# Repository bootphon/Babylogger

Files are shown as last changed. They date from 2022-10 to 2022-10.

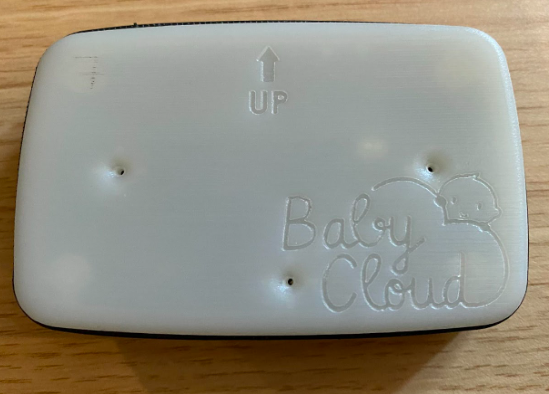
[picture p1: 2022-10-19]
pictures/babylogger.png

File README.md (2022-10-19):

# Babylogger

What is the BabyLogger?
=======================
The BabyLogger is a device used by researchers to record the child’s interactions in a secure way and to extract the audio and actimetric information.

Organization
============
All you need to fabricate a new device :
- [src](https://github.com/bootphon/Babylogger/tree/main/src) : babylogger software.
- [doc](https://github.com/bootphon/Babylogger/tree/main/doc) : the babyloger documentation with all the plans of the Babylogger box and the electronic card.

Reference
=========

- [Babylogger website](https://docs.babycloudlab.com/).

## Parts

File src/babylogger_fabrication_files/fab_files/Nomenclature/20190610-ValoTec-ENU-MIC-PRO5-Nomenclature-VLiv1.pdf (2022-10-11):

# 20190610-ValoTec-ENU-MIC-PRO5-Nomenclature-VLiv1.xlsx

Client | EHESS
Projet | ENU-MIC-PRO5
Phase | Prototype
Revision | VLiv1
Date | 10/06/2019
Designator | Description | Manufacturer | Reference Manufacturer | Supplier | Reference Supplier | Quantity | Implemented | Price | Sous total | Price /100 | Sous total | Price /1000 | Sous total | PackageRefere nce | #Column Name Error:Technology | Value | Voltage | Tolerance | #Column Name Error:Power | #Column Name Error:Resistan ce | #Column Name Error:Courant | RoHS
C1, C3 | Polarized Capacitor | AVX | TAJA106K010RNJ | Farnell | 197130 | | 2 Yes | 0,431 € | 0,86 € | 0,223 € | 0,45 € | 0,0853 € | 0,17 € | Tantal-A | | 10µF | 10V | ±10% | | | | Yes
C2, C4, C15, C18, C19, C21, C27, C28, C29, C31, C32, C35, C37, C39, C40, C41, C42, C43, C47, C49, C53, C66, C67 | Capacitor | AVX | 06035C104KAT2A | Farnell | 1301804 | 23 | Yes | 0,0284 € | 0,65 € | 0,0176 € | 0,40 € | 0,0095 € | 0,22 € | 0603 | | 100nF | 50V | ± 10% | | | | Yes
C5, C8 | Capacitor | MURATA | GRM188R61C475KAAJD | Farnell | 2611924 | | 2 No | 0,339 € | 0,00 € | 0,151 € | 0,00 € | 0,0918 € | 0,00 € | 0603 | | NC | 16V | ± 20% | | | | Yes
C6, C7, C17, C30 | Capacitor | MURATA | GRM188R61C475KAAJD | Farnell | 2611924 | | 4 Yes | 0,339 € | 1,36 € | 0,151 € | 0,60 € | 0,0918 € | 0,37 € | 0603 | | 4.7uF | 16V | ± 20% | | | | Yes
C9, C12 | Capacitor | YAGEO | CC0603KRX5R7BB225 | Farnell | 1458897 | | 2 No | 0,158 € | 0,00 € | 0,0897 € | 0,00 € | 0,0531 € | 0,00 € | 0603 | | NC | 16V | ± 10% | | | | Yes
C10, C11 | Capacitor | YAGEO | CC0603KRX5R7BB225 | Farnell | 1458897 | | 2 Yes | 0,158 € | 0,32 € | 0,0897 € | 0,18 € | 0,0531 € | 0,11 € | 0603 | | 2.2µF | 16V | ± 10% | | | | Yes
C13, C33, C34, C36, C55, C57 | Capacitor | TDK | CGA3E2X5R1A105K080AA | Farnell | 2768405 | | 6 Yes | 0,151 € | 0,91 € | 0,0731 € | 0,44 € | 0,0393 € | 0,24 € | 0603 | | 1µF | 10V | ± 10% | | | | Yes
C14 | Capacitor | TDK | CGA3E3X7R1H224K080AB | Farnell | 2210924 | | 1 Yes | 0,151 € | 0,15 € | 0,0924 € | 0,09 € | 0,0491 € | 0,05 € | 0603 | | 220nF | 50V | ± 10% | | | | Yes
C16 | Capacitor | KEMET | C1206C225K4RACTU | Farnell | 9227911 | | 1 Yes | 0,186 € | 0,19 € | 0,0848 € | 0,08 € | 0,0612 € | 0,06 € | 1206 | | 2.2µF | 16V | ± 10% | | | | Yes
C20 | Capacitor | AVX | 06035C100KAT2A | Farnell | 2332633 | | 1 Yes | 0,256 € | 0,26 € | 0,106 € | 0,11 € | 0,0408 € | 0,04 € | 0603 | | 10pF | 50V | ± 5% | | | | Yes
C22 | Capacitor | AVX | 06035C104KAT2A | Farnell | 1301804 | | 1 No | 0,0284 € | 0,00 € | 0,0176 € | 0,00 € | 0,0095 € | 0,00 € | 0603 | | 100nF | 50V | ± 10% | | | | Yes
C24, C46 | Capacitor | AVX | 06031A101JAT2A | Farnell | 1740605 | | 2 Yes | 0,0626 € | 0,13 € | 0,0273 € | 0,05 € | 0,0124 € | 0,02 € | 0603 | | 100pF | 100V | ± 5% | | | | Yes
C25, C26 | Capacitor | AVX | 04023J4R3BBSTR | Farnell | 1702754 | | 2 Yes | 0,569 € | 1,14 € | 0,306 € | 0,61 € | 0,208 € | 0,42 € | 0402 | | 4.3pF | 25V | ± 0.1pF | | | | Yes
C38 | Capacitor | AVX | 0805YD106KAT2A | Farnell | 1658880 | | 1 Yes | 0,175 € | 0,18 € | 0,10 € | 0,10 € | 0,0585 € | 0,06 € | 0805 | | 10µF | 16V | ± 10% | | | | Yes
C44 | Capacitor | AVX | 06033C103KAT2A | Farnell | 2280646 | | 1 Yes | 0,128 € | 0,13 € | 0,0427 € | 0,04 € | 0,0128 € | 0,01 € | 0603 | | 10nF | 25V | ±10% | | | | Yes
C45 | Capacitor | MURATA | GRT31CR71E106KE13L | Farnell | 2672218 | | 1 Yes | 0,527 € | 0,53 € | 0,264 € | 0,26 € | 0,109 € | 0,11 € | 1206 | | 10uF | 25V | 10% | | | | Yes
C48, C50, C54, C69 | Capacitor | KEMET | C0805C105K3RACTU | Farnell | 1637035 | | 4 Yes | 0,0976 € | 0,39 € | 0,0598 € | 0,24 € | 0,0299 € | 0,12 € | 0805 | | 1uF | 25V | ± 10% | | | | Yes
C56 | Capacitor | Murata | GRM21BR60J107ME15L | Farnell | 2494476 | | 1 Yes | 1,61 € | 1,61 € | 1,16 € | 1,16 € | 0,81 € | 0,81 € | 0805 | | 100uF | 6.3V | ± 20% | | | | Yes
C59, C60 | Capacitor | MURATA | GRM21BR61E106KA73L | Farnell | 1735530 | | 2 Yes | 0,395 € | 0,79 € | 0,233 € | 0,47 € | 0,124 € | 0,25 € | 0805 | | 10uF | 25V | ± 10% | | | | Yes
C61, C62 | Capacitor | MURATA | ZRB18AR61E106ME01L | Farnell | 2469398 | | 2 Yes | 0,448 € | 0,90 € | 0,263 € | 0,53 € | 0,14 € | 0,28 € | 0603 | | 10uF | 25V | ± 20% | | | | Yes
C63, C64, C65 | Capacitor | TDK | C2012X5R1C226M125AC | Farnell | 2525135 | | 3 Yes | 0,658 € | 1,97 € | 0,316 € | 0,95 € | 0,188 € | 0,56 € | 0805 | | 22uF | 16V | ± 10% | | | | Yes
C68 | Capacitor | JOHANSON DIELECTRICS | 202S41W222KV4E | Farnell | 1886057 | | 1 Yes | 0,342€ | 0,34 € | 0,202 € | 0,20 € | 0,0988 € | 0,10 € | 1210 | | 2.2nF | 2kV | ± 10% | | | | Yes
D1 | LED | Wurth Elektronik | 150080RS75000 | DigiKey | 732-4984-1-ND | | 1 Yes | 0,16€ | 0,16 € | 0,12820 € | 0,13 € | 0,11044 € | 0,11 € | 0805 | | | | | | | | Yes
D2 | LED | Wurth Elektronik | 150080GS75000 | Farnell | 2322076 | | 1 Yes | 0,242 € | 0,24 € | 0,168 € | 0,17 € | 0,152 € | 0,15 € | 0805 | | | | | | | | Yes
EXT1 | Batterie | Jauch | LP543450JE | Jauch | LP543450JE | | 1 No | 15 € | 0,00 € | 15 € | 0,00 € | 15 € | 0,00 €
FD1, FD2, FD3, FD4, FD6, FD7, FD8 | Fiducial Hole | | | | | | 7 Yes | 0 | 0,00 € | 0 | 0,00 € | 0 | 0,00 € | | | | | | | | | Yes
J1 | WR-COM Micro USB 2.0 Type AB Horizontal | Wurth Elektronik | 629105150921 | Farnell | 2470823 | | 1 Yes | 1,62 € | 1,62 € | 1,38 € | 1,38 € | 1,18 € | 1,18 € | | | | | | | | | Yes
J2 | WR-CRD Micro SD Card Connector Push & Push - 8 pins | Wurth Elektronik | 693071010811 | Farnell | 2081363 | | 1 Yes | 2,23 € | 2,23 € | 1,89 € | 1,89 € | 1,68 € | 1,68 € | | | | | | | | | Yes
L1 | Shielded Power Inductor | TDK | MPZ1608S300A | Farnell | 1669744 | | 1 Yes | 0,0771 € | 0,08 € | 0,0399 € | 0,04 € | 0,0232 € | 0,02 € | 0603 | | 30R/100Mhz | | ± 10ohm | | | | Yes
L2 | Inductor | Coilcraft | XFL4020-152MEB | Farnell | 994-XFL4020-152MEB | | 1 Yes | 1,93 € | 1,93 € | 1,54 € | 1,54 € | 0,858 € | 0,86 € | 4mm x 4mm x 2.1mm | | 1.5µH | | | | | | Yes
M1 | Microphone | PUI Audio. Inc | POM-2244P-C33-R | DigiKey | 668-1400-ND | | 1 Yes | 1,86 € | 1,86 € | 1,17 € | 1,17 € | 0,95590 € | 0,96 € | POM-2244P-C33-R | | | | | | | | Yes
P1 | Header, 2-Pin | MOLEX | 53261-0271 | Farnell | 2118430 | | 1 Yes | 0,686 € | 0,69 € | 0,541 € | 0,54 € | 0,488 € | 0,49 € | | | | | | | | | Yes
P2 | Header, 6-Pin | MOLEX | 78171-5006 | Mouser | 538-78171-5006 | | 1 Yes | 0,672 € | 0,67 € | 0,507 € | 0,51 € | 0,369 € | 0,37 € | | | | | | | | | Yes
P4 | Header, 4-Pin | Molex | 0524180410 | DigiKey | WM9200-ND | | 1 Yes | 0,52 € | 0,52 € | 0,37 € | 0,37 € | 0,26 € | 0,26 € | | | | | | | | | Yes
P5 | Header, 4-Pin | Molex | 0532900480 | DigiKey | WM9208-ND | | 1 Yes | 0,38 € | 0,38 € | 0,27 € | 0,27 € | 0,24 € | 0,24 € | | | | | | | | | Yes
P7 | Header, 7-Pin | Molex | 78171-5007 | Mouser | 538-78171-5007 | | 1 Yes | 0,803 € | 0,80 € | 0,606 € | 0,61 € | 0,441 € | 0,44 €
P8 | | | | | | | 1 | | 0,00 € | | 0,00 € | | 0,00 €
Q1 | MOSFET-P | VISHAY | SI2307CDS-T1-GE3 | Farnell | 1779262 | | 1 No | 0,40 € | 0,00 € | 0,261 € | 0,00 € | 0,187 € | 0,00 € | SOT23-3 | | | Vgs(th) = -1V | | | | | Yes
Q2, Q3 | MOSFET-N | FAIRCHILD SEMICONDUCTOR | 2N7002 | Farnell | 9845313 | | 2 Yes | 0,186 € | 0,37 € | 0,078 € | 0,16 € | 0,0475 € | 0,10 € | SOT23-3 | | | Vgs(th) = 2.1V | | | | | Yes
Q4 | MOSFET-P | NEXPERIA | PMV65XP,215 | Farnell | 1758119 | | 1 Yes | 0,335 € | 0,34 € | 0,163 € | 0,16 € | 0,12 € | 0,12 € | SOT23-3 | | | Vgs(th) = -750mV | | | | | Yes
R1, R28, R47, R75, R81, R92, R93, R94, R95, R96, R97 | Resistance | MULTICOMP | MC0603SAF0000T5E | Farnell | 2309111 | 11 | No | 0,0089 € | 0,00 € | 0,0072 € | 0,00 € | 0,0043 € | 0,00 € | 0603 | | 0R, NC, 0R, NC, NC, NC, NC, NC, NC, NC, NC | 50V | 1% | | | | Yes
R2, R9, R29, R30, R33, R38, R39, R40, R48, R50, R55, R60, R61, R77, R78, R79, R80, R82, R83, R86, R91 | Resistance | MULTICOMP | MC0603SAF0000T5E | Farnell | 2309111 | 21 | Yes | 0,0089 € | 0,19 € | 0,0072 € | 0,15 € | 0,0043 € | 0,09 € | 0603 | | 0R | 50V | 1% | | | | Yes
R3, R4, R5, R18, R24, R26, R34, R54, R68, R73, R74, R84, R87 | Resistance | Vishay | CRCW060310K0FKEA | Farnell | 1469748 | 13 | Yes | 0,0219 € | 0,28 € | 0,0122 € | 0,16 € | 0,0068 € | 0,09 € | 0603 | | 10k | 75V | ± 1% | | | | Yes
R6 | Resistance | Vishay | ERA3AEB1541V | Farnell | 1809752 | | 1 Yes | 0,242 € | 0,24 € | 0,114 € | 0,11 € | 0,0619 € | 0,06 € | 0603 | | 1k54 | 75V | ± 1% | | | | Yes
R7 | Resistance | Vishay | CRCW060369K8FKEA | Farnell | 2138483 | | 1 Yes | 0,0245 € | 0,02 € | 0,0166 € | 0,02 € | 0,0104 € | 0,01 € | 0603 | | 69k8 | 75V | ± 1% | | | | Yes
R8 | Resistance | VISHAY | CRCW06032K00FKEA | Farnell | 1469764 | | 1 Yes | 0,0181 € | 0,02 € | 0,0139 € | 0,01 € | 0,0088 € | 0,01 € | 0603 | | 2k | 75V | ± 1% | | | | Yes
R10, R71 | Resistance | Vishay | CRCW0603100KFKEA | Farnell | 1469649 | | 2 No | 0,0542 € | 0,00 € | 0,0217 € | 0,00 € | 0,0084 € | 0,00 € | 0603 | | 100k, NC | 75V | ± 1% | | | | Yes
R11, R12 | Resistance | MULTICOMP | MCWR06X4701FTL | Farnell | 2447385 | | 2 Yes | 0,0054 € | 0,01 € | 0,0032 € | 0,01 € | 0,0018 € | 0,00 € | 0603 | | 4.7k | 50V | 1% | | | | Yes
R13, R15, R16, R20, R21, R23, R49, R51, R57 | Resistance | VISHAY | CRCW06031K00FKEA | Farnell | 1469740 | | 9 Yes | 0,0419 € | 0,38 € | 0,0172 € | 0,15 € | 0,0073 € | 0,07 € | 0603 | | 1k | 75V | ±1%, ±1%, ±1%, ± 1%, ± 1%, ± 1%, ±1%, ±1%, ±1% | | | | Yes
R14, R90 | Resistance | WELWYN | HVC2010-1M0FT3 | Farnell | 2340627 | | 2 Yes | 1,34 € | 2,68 € | 0,921 € | 1,84 € | 0,716 € | 1,43 € | 2010 | | 1M | 2kV | ± 1% | | | | Yes
R17 | Resistance | VISHAY | WSL0603R0100FEA | Farnell | 2112794 | | 1 Yes | 0,961 € | 0,96 € | 0,40 € | 0,40 € | 0,332 € | 0,33 € | 0603 | | 10mR | 75V | ±1% | | | | Yes
R22, R35, R36, R37 | Resistance | | | | | | 4 No | 0 | 0,00 € | 0 | 0,00 € | 0 | 0,00 € | 0603 | | NC | | | | | | Yes
R31, R32 | Resistance | YAGEO | RC0603FR-072K2L | Farnell | 9238522 | | 2 Yes | 0,0239 € | 0,05 € | 0,0183 € | 0,04 € | 0,0107 € | 0,02 € | 0603 | | 2.2k | 75V | 1% | | | | Yes
R41, R70, R72, R76, R85, R98, R99 | Resistance | Vishay | CRCW0603100KFKEA | Farnell | 1469649 | | 7 Yes | 0,0542 € | 0,38 € | 0,0217 € | 0,15 € | 0,0084 € | 0,06 € | 0603 | | 100k | 75V | ± 1% | | | | Yes
R42, R43, R44, R45, R46 | Resistance | Vishay | CRCW060347K0FKEA | Farnell | 1469811 | | 5 Yes | 0,0202 € | 0,10 € | 0,0202 | 0,10 € | 0,0084 € | 0,04 € | 0603 | | 47k | 75V | ± 1% | | | | Yes
R52 | Resistance | MULTICOMP | MCWR06X4700FTL | Farnell | 2447374 | | 1 Yes | 0,0034 € | 0,00 € | 0,002 € | 0,00 € | 0,0011 € | 0,00 € | 0603 | | 470R | 50V | 1% | | | | Yes
R53, R56 | Resistance | VISHAY | CRCW06031M00FKEA | Farnell | 1469746 | | 2 Yes | 0,0419 € | 0,08 € | 0,0172 € | 0,03 € | 0,0073 € | 0,01 € | 0603 | | 1M | 75V | 1% | | | | Yes
R58, R59 | Resistance | VISHAY | CRCW060322K0FKEA | Farnell | 1469779 | | 2 Yes | 0,0542 € | 0,11 € | 0,0217 € | 0,04 € | 0,0084 € | 0,02 € | 0603 | | 22k, ? | 75V | ± 1% | | | | Yes
R88 | Resistance | PANASONIC ELECTRONIC COMPONENTS | ERJ3EKF4703V | Farnell | 2303289 | | 1 Yes | 0,0333 € | 0,03 € | 0,0243 € | 0,02 € | 0,01 € | 0,01 € | 0603 | | 470k | 75V | ± 1% | | | | Yes
R89 | Resistance | Vishay | CRCW0603150KFKEA | Farnell | 1469759 | | 1 Yes | 0,0227 € | 0,02 € | 0,0175 € | 0,02 € | 0,0095 € | 0,01 € | 0603 | | 150k | 75V | ± 1% | | | | Yes
RT1 | Thermistor | LITTELFUSE | MM103J1F | Farnell | 2888868 | | 1 Yes | 1,27 € | 1,27 € | 0,723 € | 0,72 € | 0,617 € | 0,62 €
S1 | Switch | Panasonic | EVP-AKB11A | DigiKey | P17065CT-ND | | 1 Yes | 0,54 € | 0,54 € | 0,4256 € | 0,43 € | 0,4256 € | 0,43 € | EVP-AKB11A | | | | | | | | Yes
S3 | Switch | OMRON | B3U-1000P | Farnell | 1333652 | | 1 Yes | 0,68 € | 0,68 € | 0,618 € | 0,62 € | 0,448 € | 0,45 € | B3U-1000P | | | | | | | | Yes
T1, T2, T3, T5, T11 | Test point | VERO Technologies | 20-2137 | Farnell | 8731128 | | 5 No | 0,23€ | 0,00 € | 0,23€ | 0,00 € | 0,23€ | 0,00 € | | | | | | | | | Yes
U1 | Stand-Alone System Load Sharing and Li-Ion/Li-PolymerChargeur de batterie, Batterie 1 cellule Li-Pol, Entrée 6V, Charge 4,2V / 1,1A, DFN-10 | Microchip | MCP73833-AMI/MF | Farnell | 2709765 | | 1 Yes | 0,748 € | 0,75 € | 0,565 € | 0,57 € | 0,565 € | 0,57 € | DFN-10 | | | | | | | | Yes
U2 | Linear Voltage Regulator IC Positive Fixed 1 Output 3.3V 1A 6-DFN (3x3) | STMicroelectronics | LD39100PU33RY | Digikey | 497-16700-1-ND | | 1 Yes | 1,55 € | 1,55 € | 1,08 € | 1,08 € | 0,7 € | 0,70 € | 6-DFN | | | | | | | | Yes
U3 | Jauge de batterie, Li-Ion, Li-Pol, Alimentation 2,7V à 4,35V, Interface I2C, DFN-10 | STMICROELECTRONICS | STC3115AIQT | Farnell | 2770310 | | 1 Yes | 2,73 € | 2,73 € | 1,75 € | 1,75 € | 1,19 € | 1,19 € | DFN-10 | | | | | | | | Yes
U4 | Capacitive digital sensor for relative humidity and temperature | STMicroelectronics | HTS221 | Farnell | 2433085 | | 1 Yes | 1,44 € | 1,44 € | 1,36 € | 1,36 € | 1,30 € | 1,30 € | HLGA-6L | | | | | | | | Yes
U5 | Module MEMS, iNEMO, Gyroscope 3 axes, Accéléromètre 3 axes, 1.71 V, 3.6 V, LGA, 14 Broche(s) | STMICROELECTRONICS | LSM6DSLTR | Farnell | 2761748 | | 1 Yes | 3,29 € | 3,29 € | 2,59 € | 2,59 € | 1,80 € | 1,80 € | LGA-14L | | | | | | | | Yes
U6 | MCU ARM, STM32 Family STM32L4 Series Microcontrollers, ARM Cortex-M4, 32 bits, 80 MHz, 1 MB, 320 KB | STMICROELECTRONICS | STM32L4A6RGT7 | Farnell | 2758831 | | 1 Yes | 10,95 € | 10,95 € | 8,03 € | 8,03 € | 6,54 € | 6,54 € | LQFP64 | | | | | | | | Yes
U7 | EEPROM Memory IC 2Kb (256 x 8) I²C 400kHz 900ns 8-TSSOP | STMicroelectronics | M24C02-WDW6TP | Digikey | 497-4926-1-ND | | 1 Yes | 0,12 € | 0,12 € | 0,099 € | 0,10 € | 0,093 € | 0,09 € | 8-TSSOP | | | | | | | | Yes
U8 | 1.8V, Nanopower, PUSH-PULL OUTPUT COMPARATOR | Texas Instruments | TLV3491AIDBVTG4 | Farnell | 1207299 | | 1 Yes | 1,19 € | 1,19 € | 0,646 € | 0,65 € | 0,646 € | 0,65 € | SOT23-5 | | | | | | | | Yes
U9 | Préamplificateur Microphone | MAXIM INTEGRATED PRODUCTS | MAX4466EXK+T | Farnell | 2514501 | | 1 Yes | 0,393 € | 0,39 € | 0,317 € | 0,32 € | 0,297 € | 0,30 € | | | | | | | | | Yes
U10, U11, U12, U17 | MEMS audio sensor omnidirectional digital microphone | STMicroelectronics | MP34DT06JTR | Farnell | 2980885 | | 4 Yes | 1,56 € | 6,24 € | 1,09 € | 4,36 € | 0,864 € | 3,46 € | HCLGA | | | | | | | | Yes
U14 | Very low power module for Bluetooth Smart v4.1 | STMicroelectronics | SPBTLE-RF | Mouser | 511-SPBTLE-R | | 1 Yes | 9,59 € | 9,59 € | 7,17 € | 7,17 € | 5,44 € | 5,44 € | | | | | | | | | Yes
U15 | SMD MODULE, ESP32-D0WDQ6, 32MBIT | Espressif Systems | ESP32-WROOM-32 | Digikey | 1904-1010-1-ND | | 1 Yes | 5,910 € | 5,91 € | 4,434 € | 4,43 € | 4,064 € | 4,06 € | ESP32-WROOM-32 | | | | | | | | Yes
U16 | 2-V to 16-V Buck-Boost Converter | Texas Instruments | TPS63070RNMR | Farnell | 2817379 | | 1 Yes | 2,12 € | 2,12 € | 1,50 € | 1,50 € | 1,09 € | 1,09 € | VQFN-15 | | | | | | | | Yes
Y1 | Crystal 32.768kHz | Epson Timing | NX3215SA | Digikey | 644-1156-1-ND | | 1 Yes | 0,57€ | 0,57 € | 0,4163€ | 0,42 € | 0,32865€ | 0,33 € | 3.2mmx1.5mm | | | | | | | | Yes

## TOTAL PRICE

## 79,56 € TOTAL PRICE

## 55,25 € TOTAL PRICE

42,23 €

# NOMENCLATURE ELECTRONIQUE

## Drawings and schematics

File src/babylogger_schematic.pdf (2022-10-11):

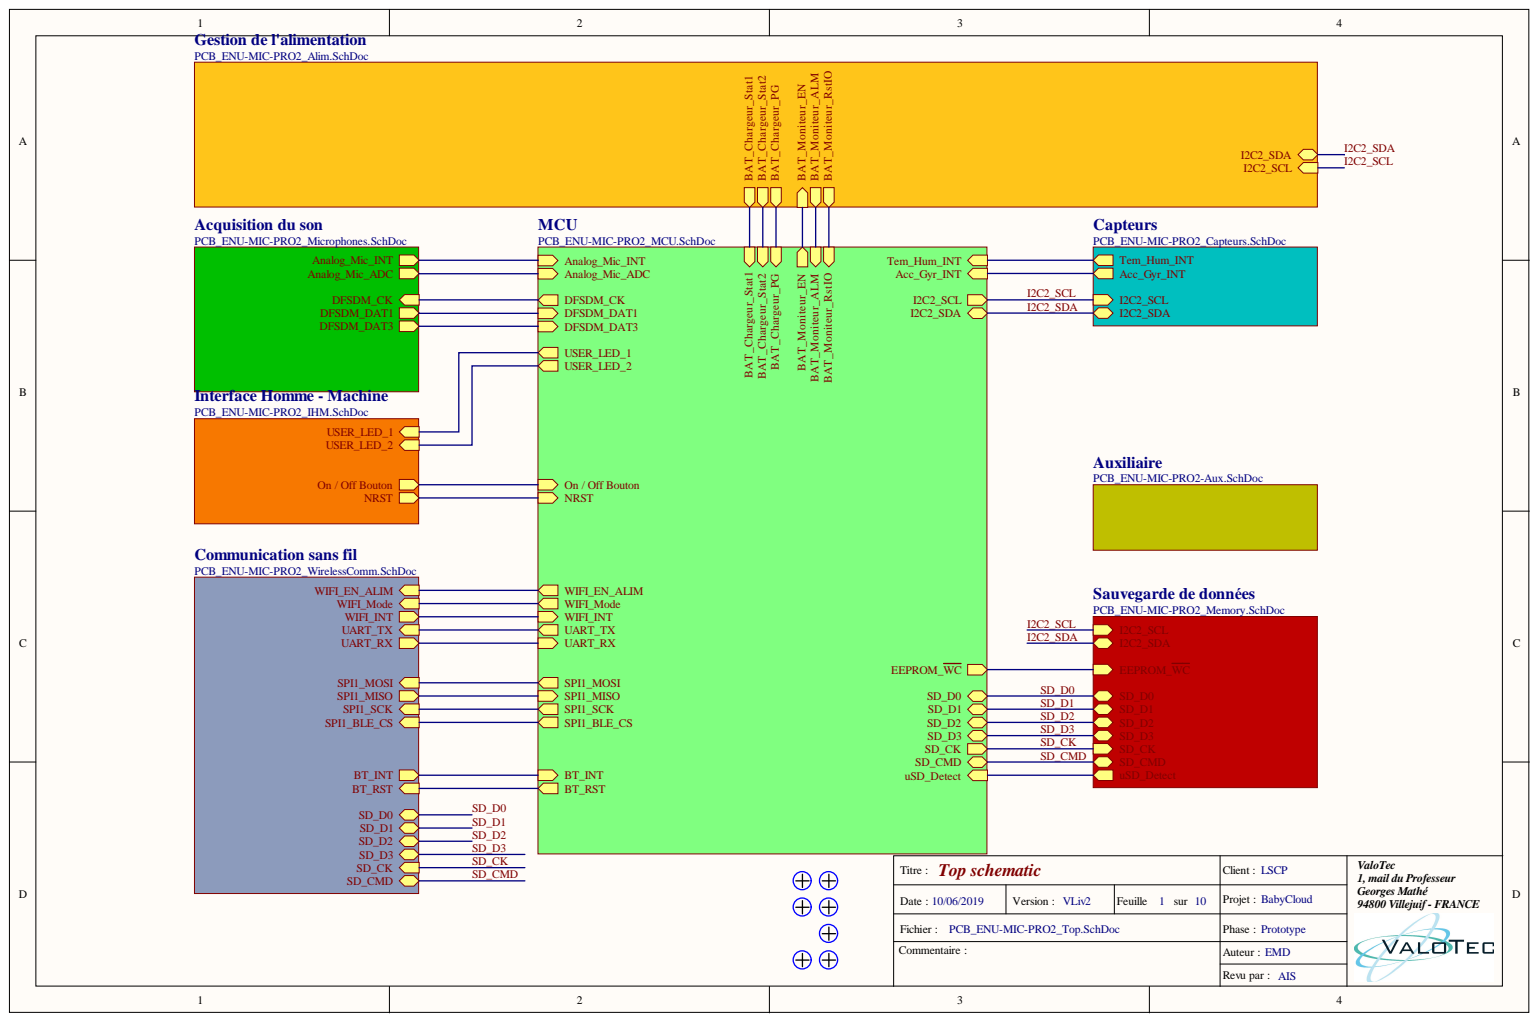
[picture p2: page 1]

Gestion de l'alimentation PCB_ENU-MIC-PRO2_Alim.SchDoc

Acquisition du son PCB_ENU-MIC-PRO2_Microphones.SchDoc

Interface Homme - Machine PCB_ENU-MIC-PRO2_IHM.SchDoc

Auxiliaire PCB_ENU-MIC-PRO2-Aux.SchDoc

Communication sans fil PCB_ENU-MIC-PRO2_WirelessComm.SchDoc

Sauvegarde de données PCB_ENU-MIC-PRO2_Memory.SchDoc

Top schematic Titre : | Client : LSCP | ValoTec 1, mail du Professeur Georges Mathé 94800 Villejuif - FRANCE

Date : 10/06/2019 | Version : VLiv2 | Feuille 1 sur 10 | Projet : BabyCloud

Fichier : PCB_ENU-MIC-PRO2_Top.SchDoc | | | Phase : Prototype

Commentaire : | | | Auteur : EMD

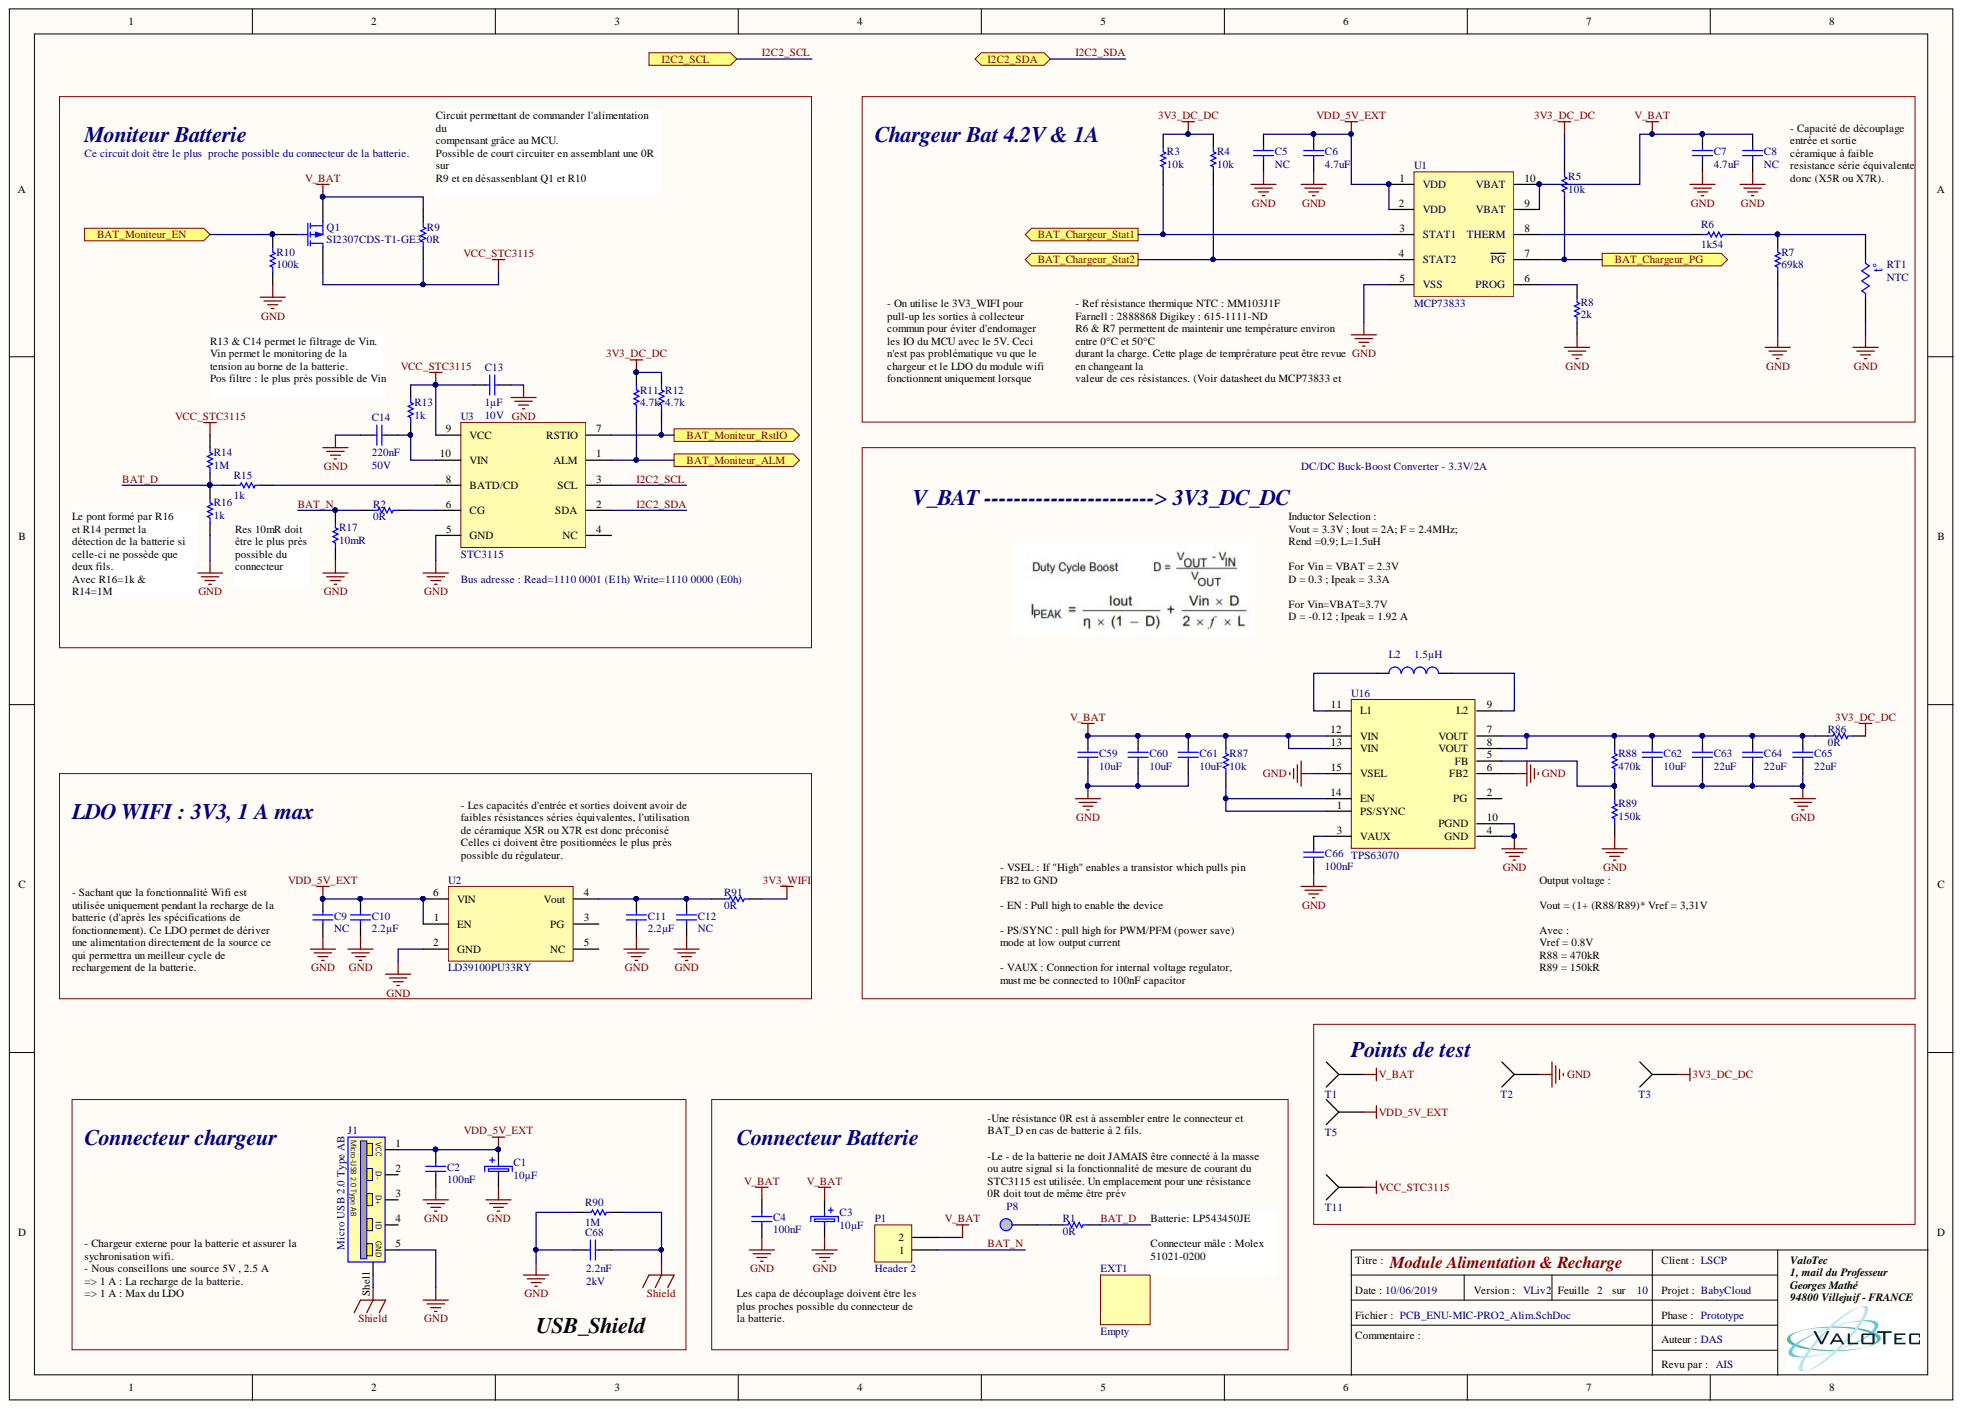
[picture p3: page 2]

Circuit permettant de commander l'alimentation
compensant grâce au MCU.
Possible de court circuiter en assemblant une 0R
sur
R9 et en désassenblant Q1 et R10

Ce circuit doit être le plus proche possible du connecteur de la batterie.

- On utilise le 3V3_WIFI pour
pull-up les sorties à collecteur
commun pour éviter d'endomager
les IO du MCU avec le 5V. Ceci
n'est pas problématique vu que le
chargeur et le LDO du module wifi
fonctionnent uniquement lorsque

- Ref résistance thermique NTC : MM103J1F
Farnell : 2888868 Digikey : 615-1111-ND
R6 & R7 permettent de maintenir une température environ
entre 0°C et 50°C
durant la charge. Cette plage de temprérature peut être revue
en changeant la
valeur de ces résistances. (Voir datasheet du MCP73833 et

R13 & C14 permet le filtrage de Vin.
Vin permet le monitoring de la
tension au borne de la batterie.
Pos filtre : le plus près possible de Vin

DC/DC Buck-Boost Converter - 3.3V/2A

Le pont formé par R16
et R14 permet la
détection de la batterie si
celle-ci ne possède que
deux fils.
Avec R16=1k &

Bus adresse : Read=1110 0001 (E1h) Write=1110 0000 (E0h)

- Les capacités d'entrée et sorties doivent avoir de
faibles résistances séries équivalentes, l'utilisation
de céramique X5R ou X7R est donc préconisé
Celles ci doivent être positionnées le plus près
possible du régulateur.

- VSEL : If "High" enables a transistor which pulls pin
FB2 to GND

- Sachant que la fonctionnalité Wifi est
utilisée uniquement pendant la recharge de la
batterie (d'après les spécifications de
fonctionnement). Ce LDO permet de dériver
une alimentation directement de la source ce
qui permettra un meilleur cycle de
rechargement de la batterie.

- EN : Pull high to enable the device

- PS/SYNC : pull high for PWM/PFM (power save)
mode at low output current

- VAUX : Connection for internal voltage regulator,
must me be connected to 100nF capacitor

-Une résistance 0R est à assembler entre le connecteur et
BAT_D en cas de batterie à 2 fils.

Micro USB 2.0 Type AB

Micro-USB 2.0 Type AB

-Le - de la batterie ne doit JAMAIS être connecté à la masse
ou autre signal si la fonctionnalité de mesure de courant du
STC3115 est utilisée. Un emplacement pour une résistance
0R doit tout de même être prév

- Chargeur externe pour la batterie et assurer la
sychronisation wifi.
- Nous conseillons une source 5V , 2.5 A
=> 1 A : La recharge de la batterie.
=> 1 A : Max du LDO

Titre : Module Alimentation & Recharge | Client : LSCP | ValoTec 1, mail du Professeur Georges Mathé 94800 Villejuif - FRANCE

Les capa de découplage doivent être les
plus proches possible du connecteur de
la batterie.

Date : 10/06/2019 | Version : VLiv2 | Feuille 2 sur 10 | Projet : BabyCloud

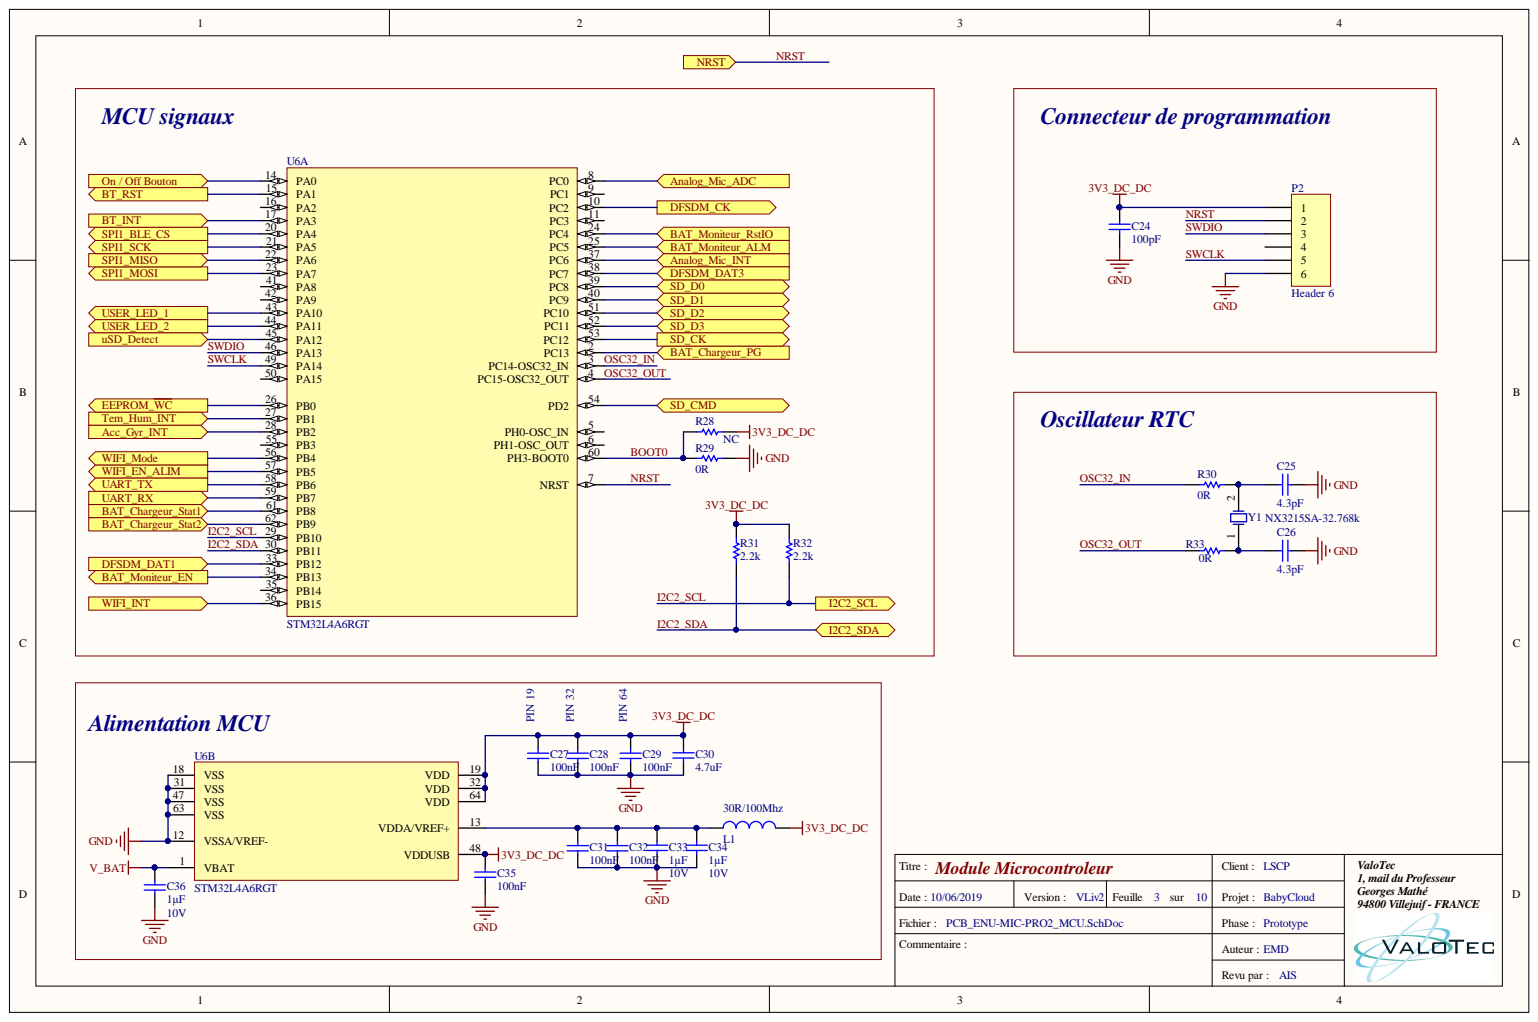
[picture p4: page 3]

Date : 10/06/2019 | Version : VLiv2 | Feuille 3 sur 10 | Projet : BabyCloud

Fichier : PCB_ENU-MIC-PRO2_MCU.SchDoc | | | Phase : Prototype
Commentaire : | | | Auteur : EMD

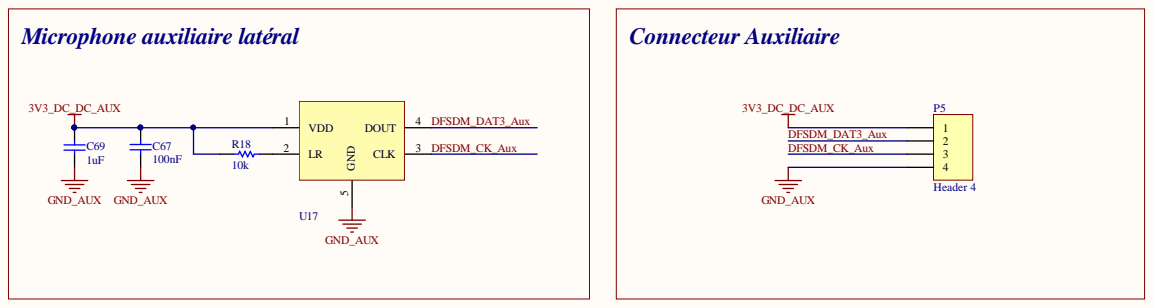
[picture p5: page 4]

Titre : P CB A uxiliaire | C lient : L S C P | Valo Te c 1 , m a il du Professe u r Ge o rg es Math é 948 0 0 Villeju if -FRA NCE

Da t e : 10/ 0 6/2 0 1 9 | Vers ion : VL iv2 | F e u ille 4 sur 1 0 | Proj e t : B a b y C lo u d

F ichi er : P C B _ENU-M I C-P RO2-A u x . S chDo c | | | P h a s e : Pro tot ype
C o mm e n t a ire : | | | Au t eur : DA SAI

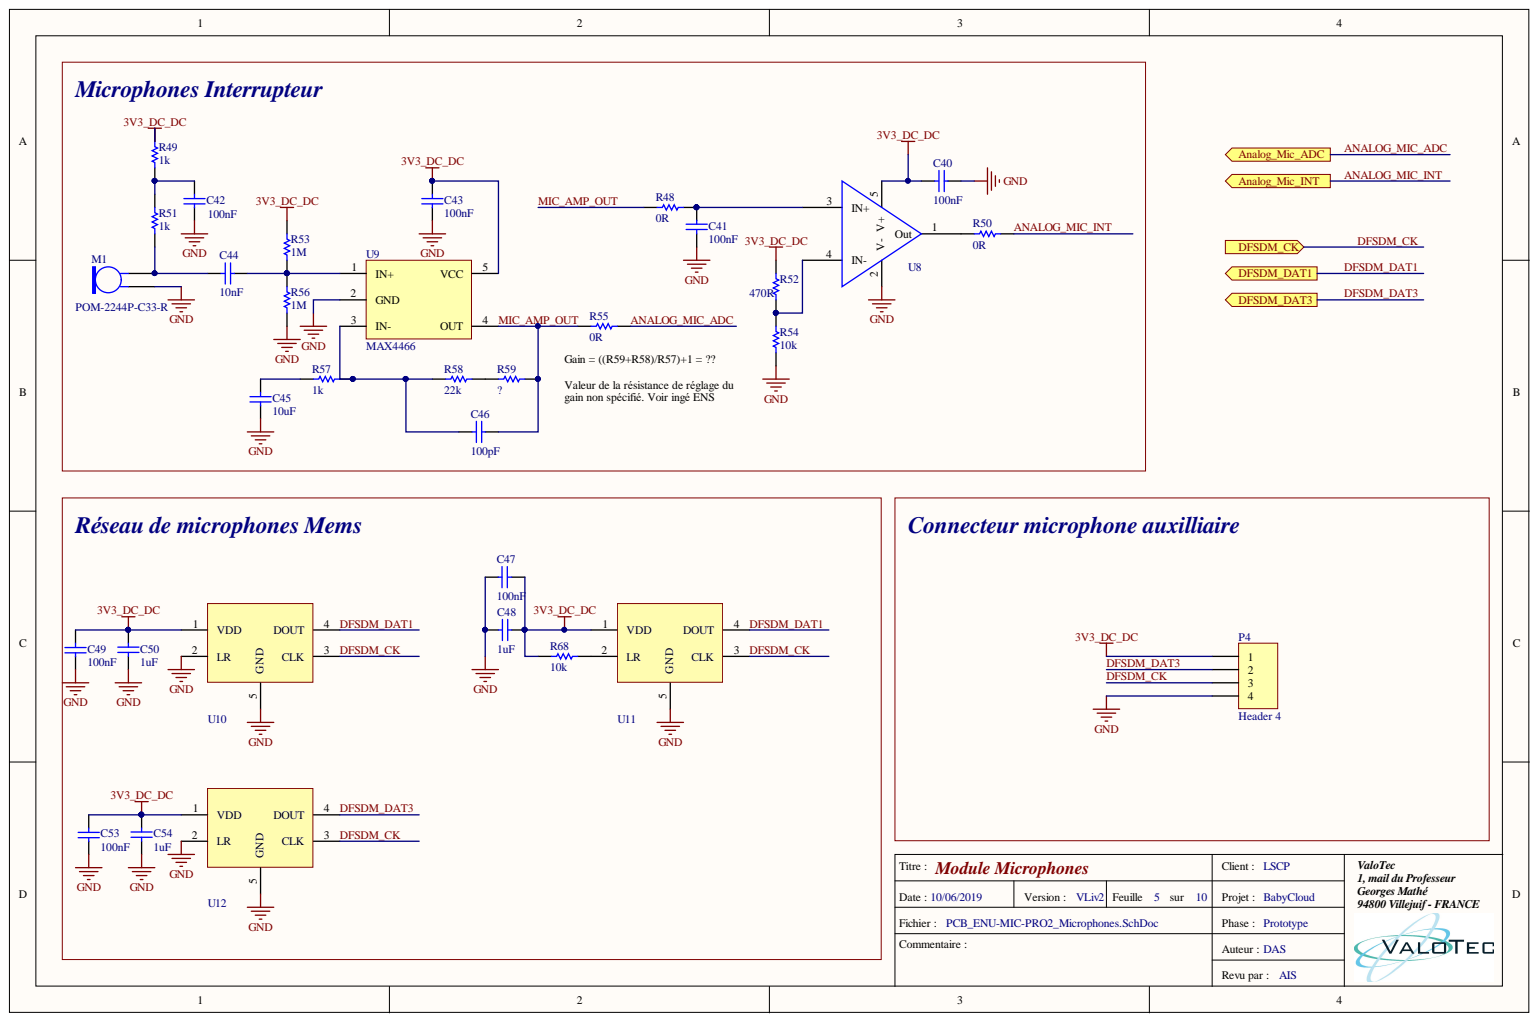
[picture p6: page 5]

Valeur de la résistance de réglage du
gain non spécifié. Voir ingé ENS

Réseau de microphones Mems

Titre : Module Microphones | Client : LSCP | ValoTec 1, mail du Professeur Georges Mathé 94800 Villejuif - FRANCE

Date : 10/06/2019 | Version : VLiv2 | Feuille 5 sur 10 | Projet : BabyCloud

Fichier : PCB_ENU-MIC-PRO2_Microphones.SchDoc | | | Phase : Prototype
Commentaire : | | | Auteur : DAS

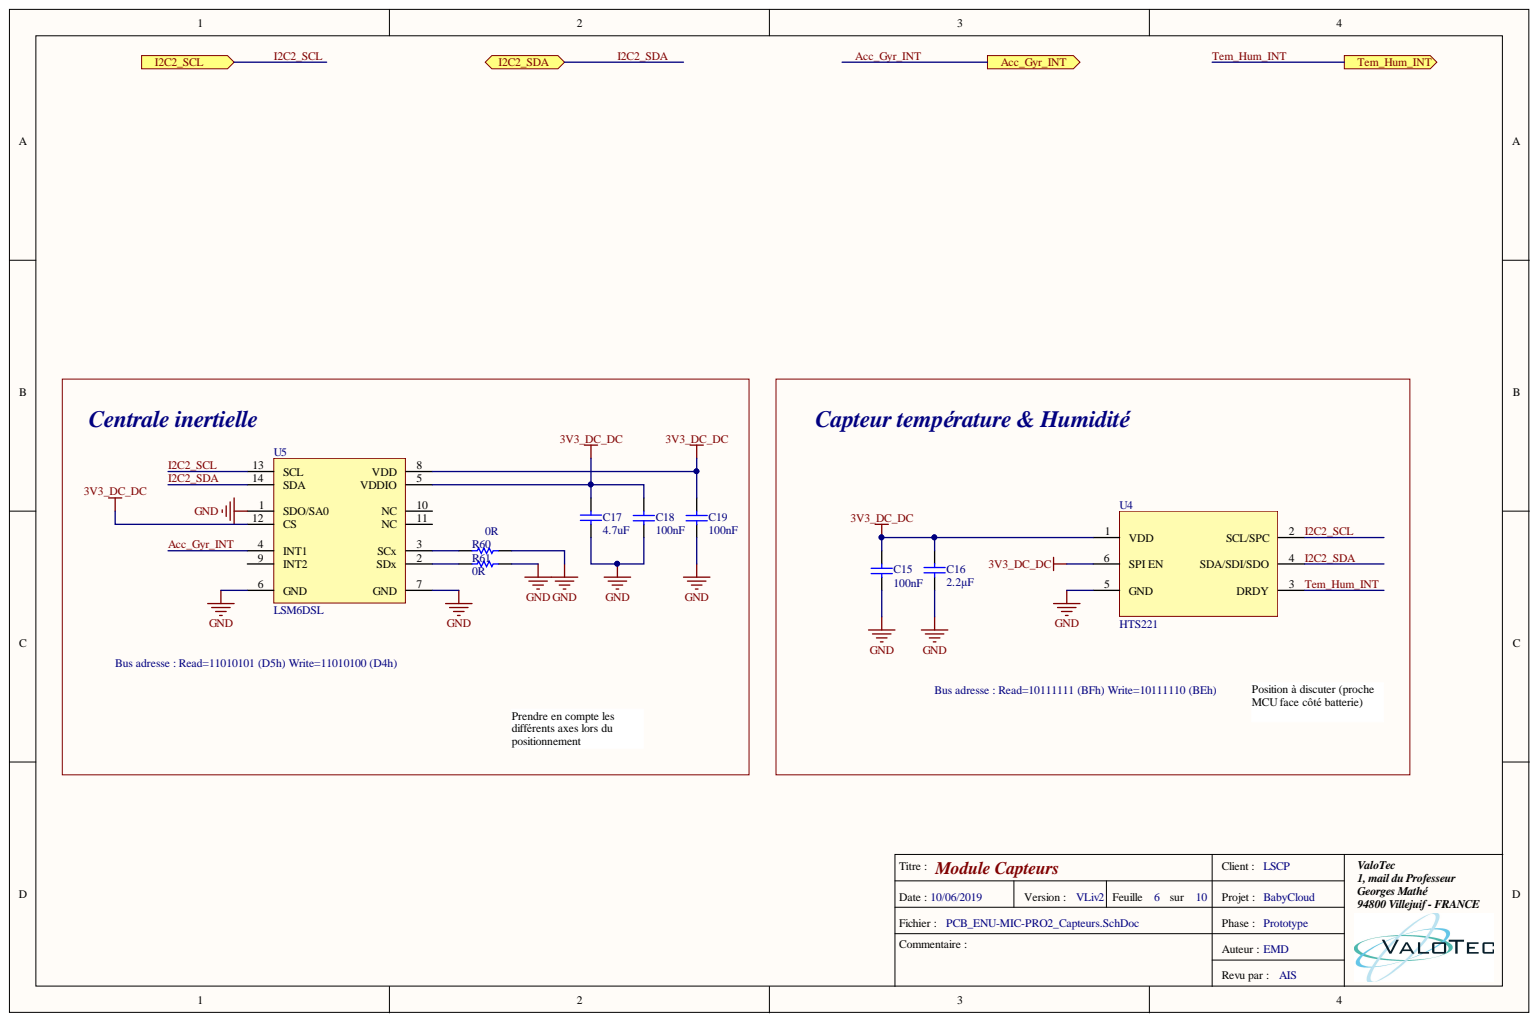
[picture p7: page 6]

Bus adresse : Read=11010101 (D5h) Write=11010100 (D4h)

MCU face côté batterie)
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

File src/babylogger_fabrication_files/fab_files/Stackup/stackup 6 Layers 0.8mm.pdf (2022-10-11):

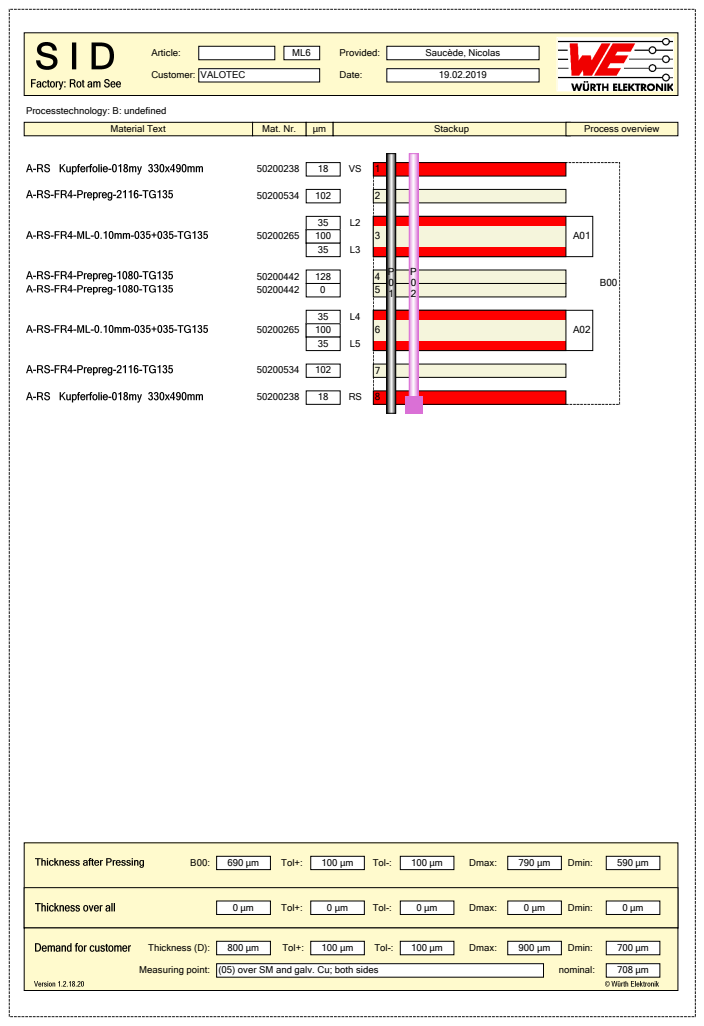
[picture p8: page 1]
Article:; Customer:; VALOTEC; Provided:; Saucède, Nicolas; Date:; Processtechnology: B: undefined; Material Text; Mat. Nr.; Stackup; Process overview; Tol+:; Tol-:; Dmax:; Dmin:; Thickness (D):; Measuring point:; (05) over SM and galv. Cu; both sides; nominal:

35 | L2 | 3 | | A01
50200265 | 100

35 | L4 | 6 | | A02

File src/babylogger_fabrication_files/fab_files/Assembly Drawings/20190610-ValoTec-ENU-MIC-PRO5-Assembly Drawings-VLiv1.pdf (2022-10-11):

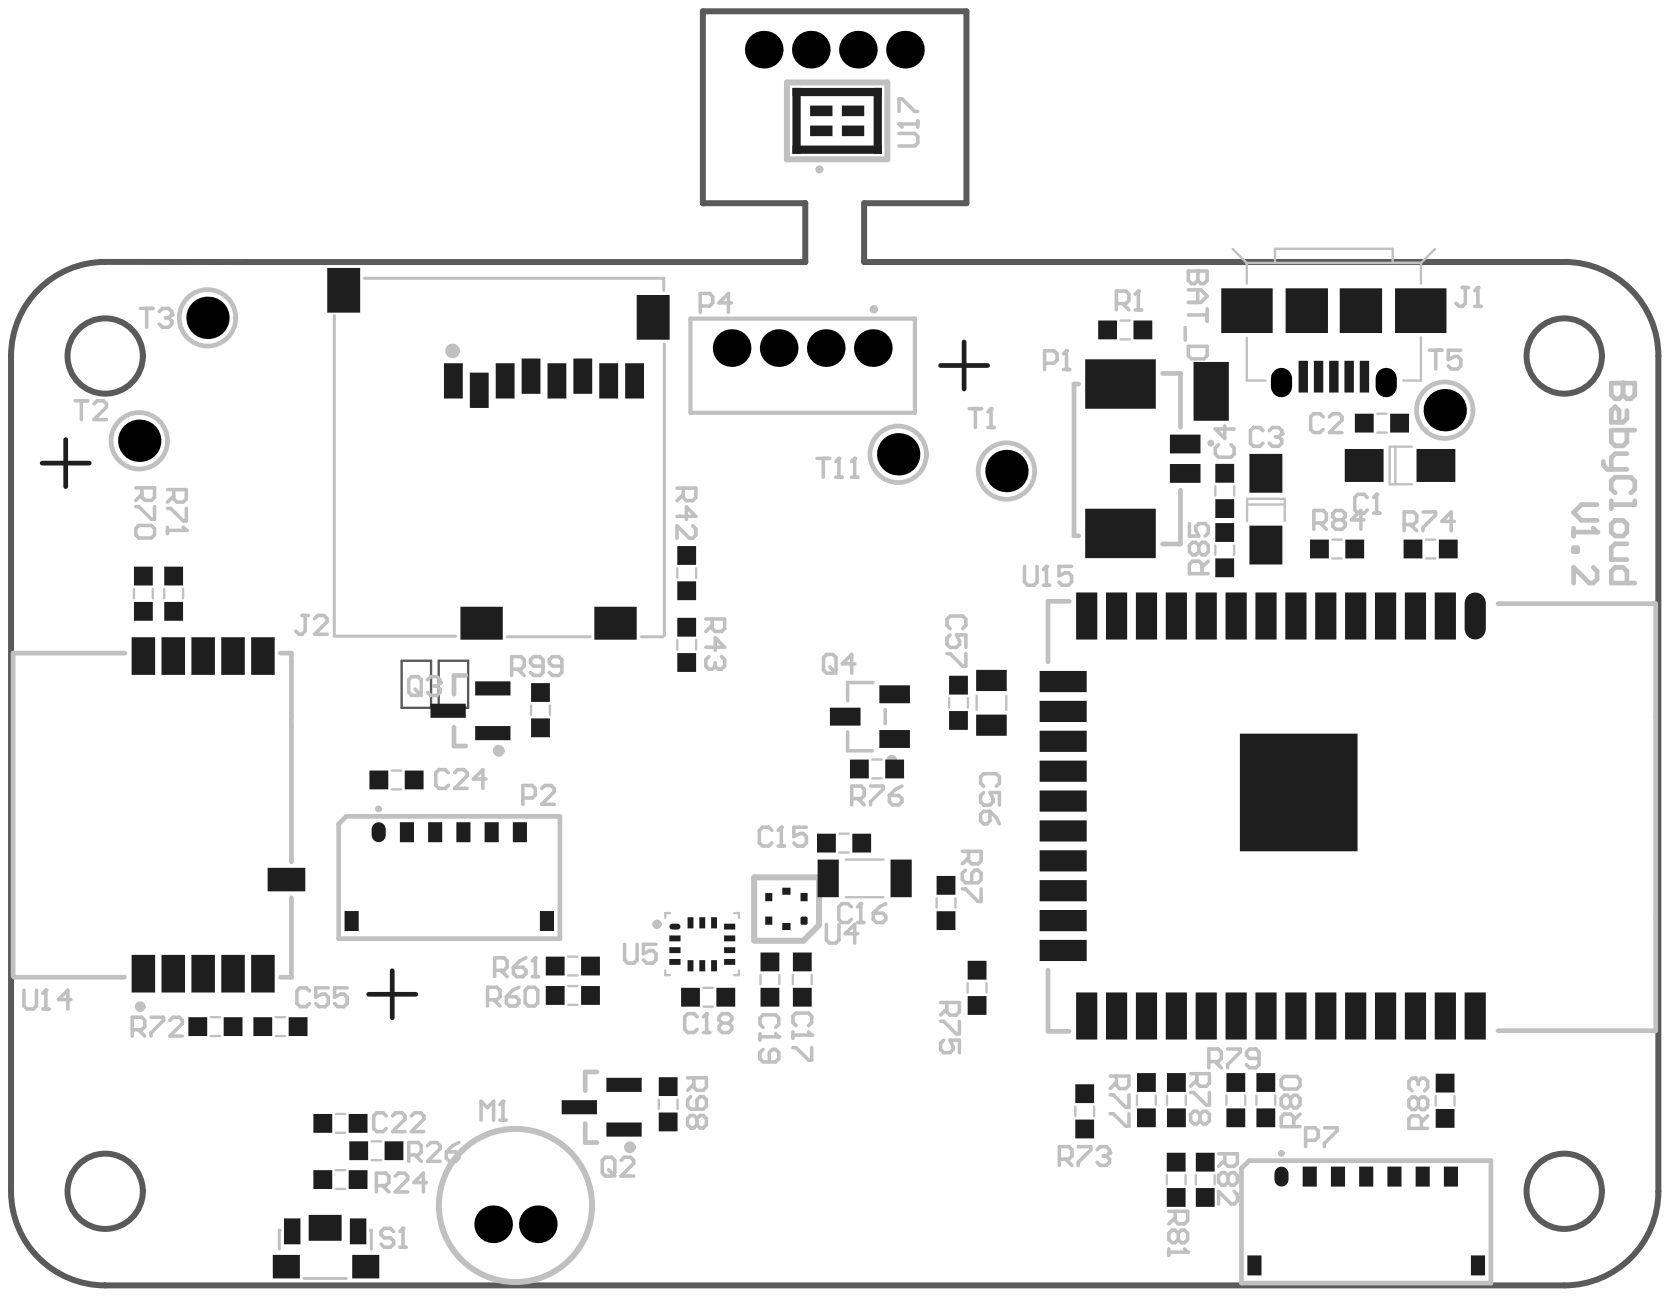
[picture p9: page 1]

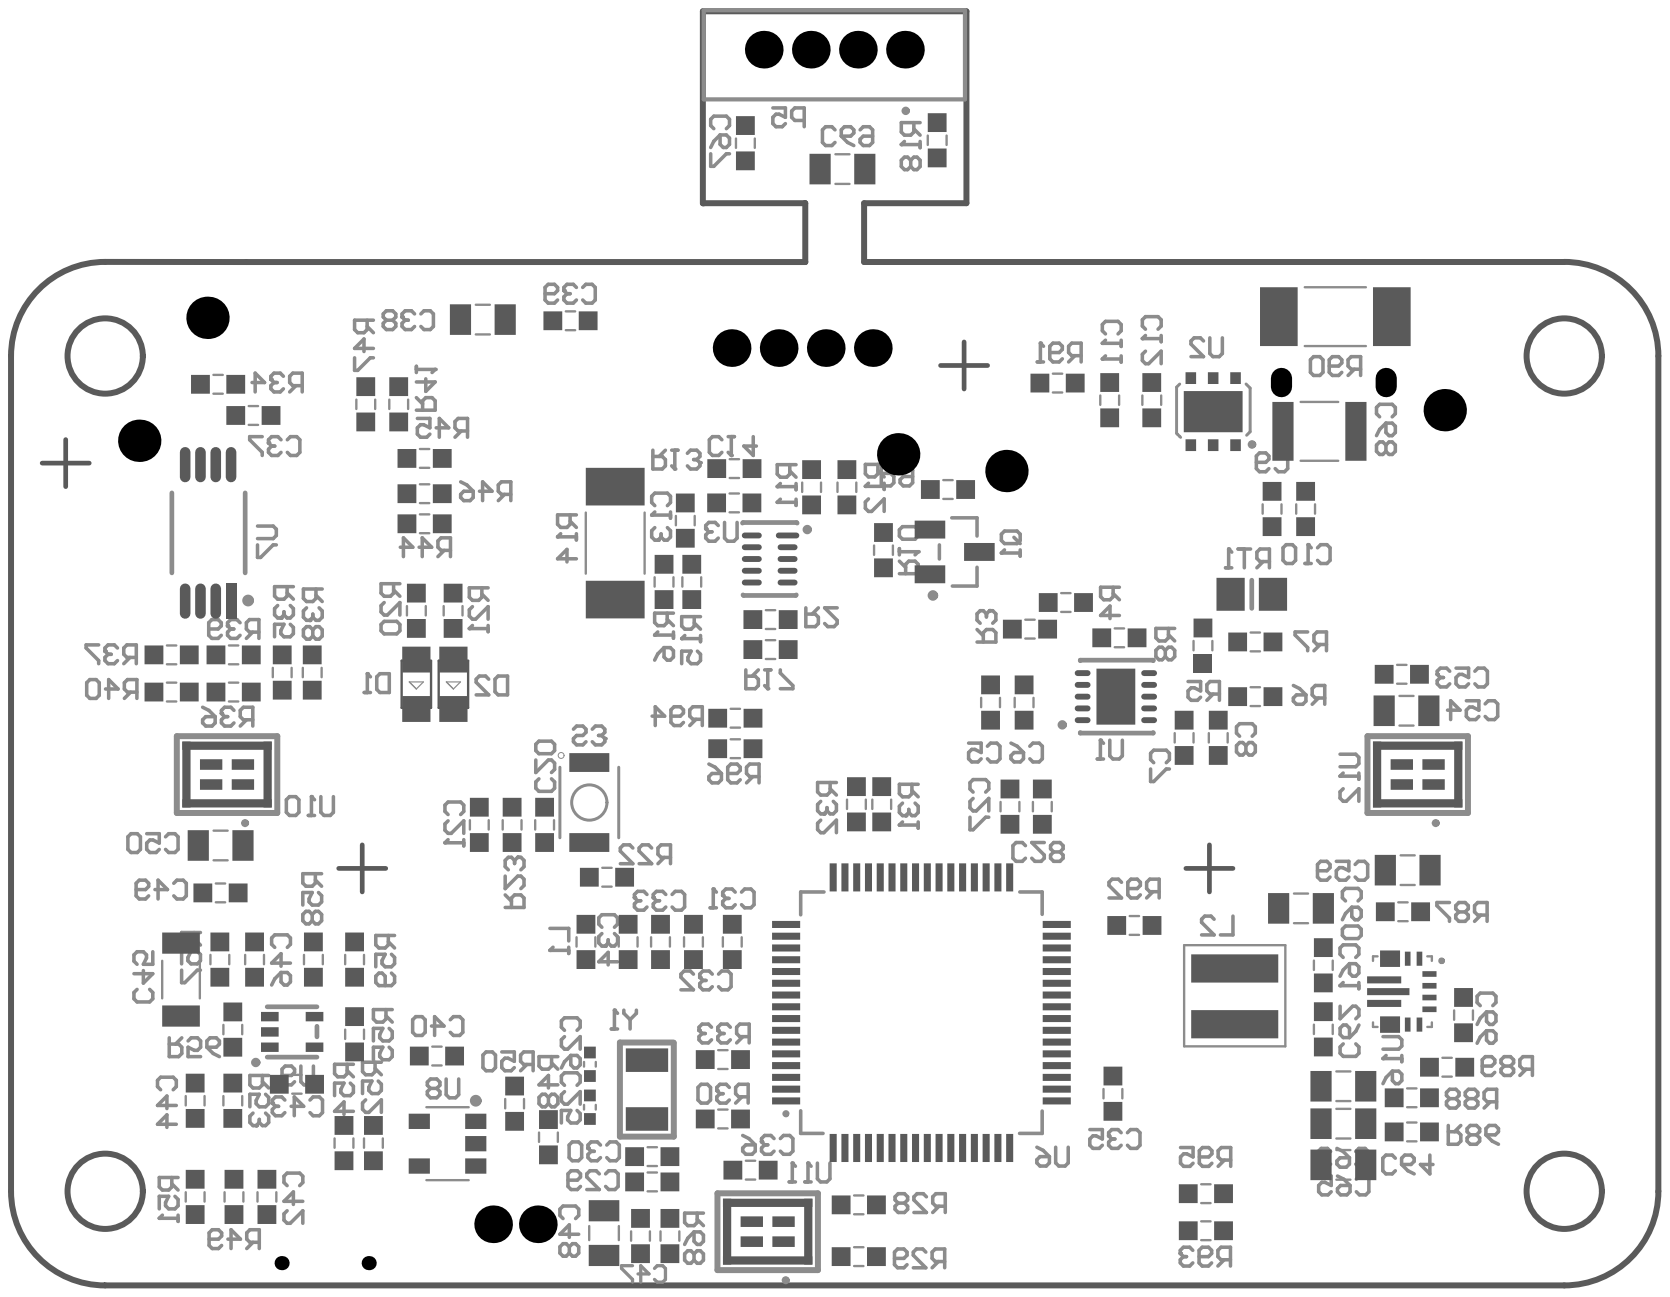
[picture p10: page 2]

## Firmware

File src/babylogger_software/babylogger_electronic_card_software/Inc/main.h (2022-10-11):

/* USER CODE BEGIN Header */
/**
  ******************************************************************************
  * @file           : main.h
  * @brief          : Header for main.c file.
  *                   This file contains the common defines of the application.
  ******************************************************************************
  * @attention
  *
  * <h2><center>&copy; Copyright (c) 2019 STMicroelectronics.
  * All rights reserved.</center></h2>
  *
  * This software component is licensed by ST under Ultimate Liberty license
  * SLA0044, the "License"; You may not use this file except in compliance with
  * the License. You may obtain a copy of the License at:
  *                             www.st.com/SLA0044
  *
  ******************************************************************************
  */
/* USER CODE END Header */

/* Define to prevent recursive inclusion -------------------------------------*/
#ifndef __MAIN_H
#define __MAIN_H

#ifdef __cplusplus
extern "C" {
#endif

/* Includes ------------------------------------------------------------------*/
#include "stm32l4xx_hal.h"
#include "stdio.h"	
#include <stdint.h> 
/*#include "fatfs.h"
#include "ff.h"
#include "ff_gen_drv.h"
#include "sd_diskio.h" */
//#include "DFSDM.h"
#include "Acquisition_Audio.h"
#include "IHM.h"
#include "RTC.h"
#include "UART_com.h"
#include "hci_tl_interface.h"
#include "UART_DEBUG.h"
//#include "Crypt.h"
/* Private includes ----------------------------------------------------------*/
/* USER CODE BEGIN Includes */

/* USER CODE END Includes */

/* Exported types ------------------------------------------------------------*/
/* USER CODE BEGIN ET */

/* USER CODE END ET */

/* Exported constants --------------------------------------------------------*/
/* USER CODE BEGIN EC */

/* USER CODE END EC */

/* Exported macro ------------------------------------------------------------*/
/* USER CODE BEGIN EM */

/* USER CODE END EM */

/* Exported functions prototypes ---------------------------------------------*/
void Error_Handler(void);

/* USER CODE BEGIN EFP */

/* USER CODE END EFP */

/* Private defines -----------------------------------------------------------*/
#define B1_Pin GPIO_PIN_13
#define B1_GPIO_Port GPIOC
#define USART_TX_Pin GPIO_PIN_2
#define USART_TX_GPIO_Port GPIOA
#define USART_RX_Pin GPIO_PIN_3
#define USART_RX_GPIO_Port GPIOA
#define LD2_Pin GPIO_PIN_5
#define LD2_GPIO_Port GPIOA
#define TMS_Pin GPIO_PIN_13
#define TMS_GPIO_Port GPIOA
#define TCK_Pin GPIO_PIN_14
#define TCK_GPIO_Port GPIOA
#define SWO_Pin GPIO_PIN_3
#define SWO_GPIO_Port GPIOB
/* USER CODE BEGIN Private defines */

/* USER CODE END Private defines */

#ifdef __cplusplus
}
#endif

#endif /* __MAIN_H */

/************************ (C) COPYRIGHT STMicroelectronics *****END OF FILE****/

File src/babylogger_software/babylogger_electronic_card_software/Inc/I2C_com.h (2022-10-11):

#include "stm32l4xx_hal.h"




#define EEPROM_ADDR 0xA0


#define SENSOR_I2C_X 					I2C4
#define SENSOR_I2C_PORT				GPIOB
#define SENSOR_I2C_SDA				GPIO_PIN_11
#define SENSOR_I2C_SCL				GPIO_PIN_10
#define SENSOR_I2C_AF 				GPIO_AF3_I2C4

int32_t I2C_ReadReg(uint16_t DevAddr, uint16_t Reg, uint8_t *pData, uint16_t Length) ;
int32_t I2C_WriteReg(uint16_t DevAddr, uint16_t Reg, uint8_t *pData, uint16_t Length);
int32_t I2C_Init(void);
int32_t I2C_DeInit(void);
int32_t SENSOR_IO_GetTick(void);
void SENSOR_DMA_Start(uint16_t DevAddress, uint16_t MemAddress, uint16_t MemAddSize, uint8_t *pData, uint16_t Size);

//Link fonctions drivers
#define SENSOR_I2C_Init I2C_Init
#define SENSOR_I2C_DeInit I2C_DeInit
#define SENSOR_I2C_ReadReg I2C_ReadReg
#define SENSOR_I2C_WriteReg I2C_WriteReg
#define SENSOR_GetTick SENSOR_IO_GetTick


/* BSP Common Error codes */
#define BSP_ERROR_NONE                    0
#define BSP_ERROR_NO_INIT                -1
#define BSP_ERROR_WRONG_PARAM            -2
#define BSP_ERROR_BUSY                   -3
#define BSP_ERROR_PERIPH_FAILURE         -4
#define BSP_ERROR_COMPONENT_FAILURE      -5
#define BSP_ERROR_UNKNOWN_FAILURE        -6
#define BSP_ERROR_UNKNOWN_COMPONENT      -7 
#define BSP_ERROR_BUS_FAILURE            -8
#define BSP_ERROR_CLOCK_FAILURE          -9
#define BSP_ERROR_MSP_FAILURE            -10
#define BSP_ERROR_FEATURE_NOT_SUPPORTED      -11
   
   
/* BSP BUS error codes */
#define BSP_ERROR_BUS_TRANSACTION_FAILURE    -100
#define BSP_ERROR_BUS_ARBITRATION_LOSS       -101
#define BSP_ERROR_BUS_ACKNOWLEDGE_FAILURE    -102
#define BSP_ERROR_BUS_PROTOCOL_FAILURE       -103

#define BSP_ERROR_BUS_MODE_FAULT             -104
#define BSP_ERROR_BUS_FRAME_ERROR            -105
#define BSP_ERROR_BUS_CRC_ERROR              -106
#define BSP_ERROR_BUS_DMA_FAILURE            -107

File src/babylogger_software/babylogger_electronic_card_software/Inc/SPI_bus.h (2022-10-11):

/**
  ******************************************************************************
  * @file           : custom_bus.h
  * @brief          : header file for the BSP BUS IO driver
  ******************************************************************************
  * @attention
  *
  * <h2><center>&copy; Copyright (c) 2019 STMicroelectronics.
  * All rights reserved.</center></h2>
  *
  * This software component is licensed by ST under Ultimate Liberty license
  * SLA0044, the "License"; You may not use this file except in compliance with
  * the License. You may obtain a copy of the License at:
  *                             www.st.com/SLA0044
  *
  ******************************************************************************
*/

/* Define to prevent recursive inclusion -------------------------------------*/
#ifndef CUSTOM_BUS_H
#define CUSTOM_BUS_H

#ifdef __cplusplus
 extern "C" {
#endif

/* Includes ------------------------------------------------------------------*/
#include "custom_conf.h"
#include "custom_errno.h"

/** @addtogroup BSP
  * @{
  */

/** @addtogroup CUSTOM
  * @{
  */

/** @defgroup CUSTOM_BUS CUSTOM BUS
  * @{
  */

/** @defgroup CUSTOM_BUS_Exported_Constants CUSTOM BUS Exported Constants
  * @{
  */

#define BUS_SPI3_INSTANCE SPI1
#define BUS_SPI3_SCK_GPIO_PIN GPIO_PIN_5
#define BUS_SPI3_SCK_GPIO_AF GPIO_AF5_SPI1
#define BUS_SPI3_SCK_GPIO_CLK_ENABLE() __HAL_RCC_GPIOA_CLK_ENABLE()
#define BUS_SPI3_SCK_GPIO_PORT GPIOA
#define BUS_SPI3_SCK_GPIO_CLK_DISABLE() __HAL_RCC_GPIOA_CLK_DISABLE()
#define BUS_SPI3_MISO_GPIO_PIN GPIO_PIN_6
#define BUS_SPI3_MISO_GPIO_AF GPIO_AF5_SPI1
#define BUS_SPI3_MISO_GPIO_CLK_ENABLE() __HAL_RCC_GPIOA_CLK_ENABLE()
#define BUS_SPI3_MISO_GPIO_PORT GPIOA
#define BUS_SPI3_MISO_GPIO_CLK_DISABLE() __HAL_RCC_GPIOA_CLK_DISABLE()
#define BUS_SPI3_MOSI_GPIO_PIN GPIO_PIN_7
#define BUS_SPI3_MOSI_GPIO_AF GPIO_AF5_SPI1
#define BUS_SPI3_MOSI_GPIO_CLK_ENABLE() __HAL_RCC_GPIOA_CLK_ENABLE()
#define BUS_SPI3_MOSI_GPIO_PORT GPIOA
#define BUS_SPI3_MOSI_GPIO_CLK_DISABLE() __HAL_RCC_GPIOA_CLK_DISABLE()
#ifndef BUS_SPI3_POLL_TIMEOUT
  #define BUS_SPI3_POLL_TIMEOUT                   0x1000U
#endif
/* SPI3 Baud rate in bps  */
#ifndef BUS_SPI3_BAUDRATE   
   #define BUS_SPI3_BAUDRATE   10000000U /* baud rate of SPIn = 10 Mbps*/
#endif

/**
  * @}
  */

/** @defgroup CUSTOM_BUS_Private_Types CUSTOM BUS Private types
  * @{
  */
#if (USE_HAL_SPI_REGISTER_CALLBACKS == 1) 
typedef struct
{
  pSPI_CallbackTypeDef  pMspInitCb;
  pSPI_CallbackTypeDef  pMspDeInitCb;
}BSP_SPI_Cb_t;
#endif /* (USE_HAL_SPI_REGISTER_CALLBACKS == 1) */
/**
  * @}
  */
  
/** @defgroup CUSTOM_LOW_LEVEL_Exported_Variables LOW LEVEL Exported Constants
  * @{
  */

extern SPI_HandleTypeDef hspi3;

/**
  * @}
  */

/** @addtogroup CUSTOM_BUS_Exported_Functions
  * @{
  */    

/* BUS IO driver over SPI Peripheral */
HAL_StatusTypeDef MX_SPI3_Init(SPI_HandleTypeDef* hspi);
int32_t BSP_SPI3_Init(void);
int32_t BSP_SPI3_DeInit(void);
int32_t BSP_SPI3_Send(uint8_t *pData, uint16_t Length);
int32_t BSP_SPI3_Recv(uint8_t *pData, uint16_t Length);
int32_t BSP_SPI3_SendRecv(uint8_t *pTxData, uint8_t *pRxData, uint16_t Length);
#if (USE_HAL_SPI_REGISTER_CALLBACKS == 1)
int32_t BSP_SPI3_RegisterDefaultMspCallbacks (void);
int32_t BSP_SPI3_RegisterMspCallbacks (BSP_SPI_Cb_t *Callbacks);
#endif /* (USE_HAL_SPI_REGISTER_CALLBACKS == 1) */

int32_t BSP_GetTick(void);

/**
  * @}
  */

/**
  * @}
  */

/**
  * @}
  */

/**
  * @}
  */
#ifdef __cplusplus
}
#endif

#endif /* CUSTOM_BUS_H */

/************************ (C) COPYRIGHT STMicroelectronics *****END OF FILE****/

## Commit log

2022-10-11 fabrication files
    [20190610-ValoTec-ENU-MIC-PRO5-Nomenclature-VLiv1.xlsx, PCB_ENU-MIC-PRO2_PCB.GBL, PCB_ENU-MIC-PRO2_PCB.GBO, PCB_ENU-MIC-PRO2_PCB.GBP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]
2022-10-12 Fab folder
    [20190610-ValoTec-ENU-MIC-PRO5-Nomenclature-VLiv1.xlsx, PCB_ENU-MIC-PRO2_PCB.GBL, PCB_ENU-MIC-PRO2_PCB.GBO, PCB_ENU-MIC-PRO2_PCB.GBP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]
